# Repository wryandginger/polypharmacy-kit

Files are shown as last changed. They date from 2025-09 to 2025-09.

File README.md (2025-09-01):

# A 3D Printable Polypharmacy Kit
This is designed to be a sustainable and self-managed version of [polypharmacy](https://en.wikipedia.org/wiki/Polypharmacy) services by PillPack, SimpleDose, MedPack, etc.

I needed to create this because all of these services have shut down (or become significantly worse) due to late-stage capitalism, [enshittification](https://en.wikipedia.org/wiki/Enshittification), and unsustainable business practices. 

In my case, Amazon's aquisition and integration of PillPack has resulted in some of my medications now being "ineligible" for PillPack without warning or alternatives.
For a service designed for folks who need medication management help, (i.e. the elderly and chronically ill) this is deeply disappointing and frustrating.

The goal with this project is to have a whole medication system that functions like PillPack, but wastes less plastic and gives Amazon less of your personal data.

This is an elaborate remix of [TOXXIC407's Pill Organizer](https://www.thingiverse.com/thing:6817349), but significantly smaller (60%) in size and a few extra parts.

I tested this on a FlashForge Adventurer 5M Pro using natural PLA and Food Safe PLA printed at .12mm Fine Settings with 15% infill. 
I recommend using certified Food Safe PLA for obvious reasons, but I'm not a medical doctor or a lawyer, so you print at your own risk.

I'm mostly posting this because I have a habit of deleting and overwriting project STL files and I don't want to lose this (again).

# Instructions
1. Download the pillbox_daybase.stl and monday.stl files
2. Verify that the size is what you want. (This can hold about 9 small RX tablets, but you may have bigger pills.)
3. Scale up as needed. (This is as small as possible, increasing the scale should work without much issue.)
4. Print the base and Monday lid on your 3D printer. Verify that things fit together the way you want.
5. Print 28 more bases
6. Print 3 more Monday lids, print 4 Tuesday lids, 4 Wednesday lids, etc. until you have 28 lids for 28 bases.
7. Print 4 casettes and 4 casette lids
8. (Optional) Print a blank lid for an extra day.
9. (Optional) Print 1-4 medtrays to help with refilling or acting as a 1-week home caddy.

# Assembly and Use 
1. Slide your lid on to each box and make sure no box is cracked. I recommend assembling each box right as the lid finishes printing to minimize warping.
2. Each casette holds one week of medication in a small pocket sized box. (Consider printing a label with RX numbers and medication names for travel)
3. Neatly stack 7 days, with the first day at the bottom. Slowly slide the casette over 7 days, then tilt and close with the lid.
4. Dispense by removing the lid and tilting toward your hand like you would serve candy. Each day should dispense individually from the casette almost like a pez dispenser, but using gravity.
5. Repeat this 4 times to produce 4 casettes with 28 days of pre-sorted medication, 5 times gives you space for 35 boxes, etc.
6. (Optional) Use a [tilt or vibration sensor](https://www.amazon.com/Aqara-Vibration-Sensor-Automation-Compatible/dp/B07PJT939B/) to track and verify medication compliance (sample automation YAML coming soon)

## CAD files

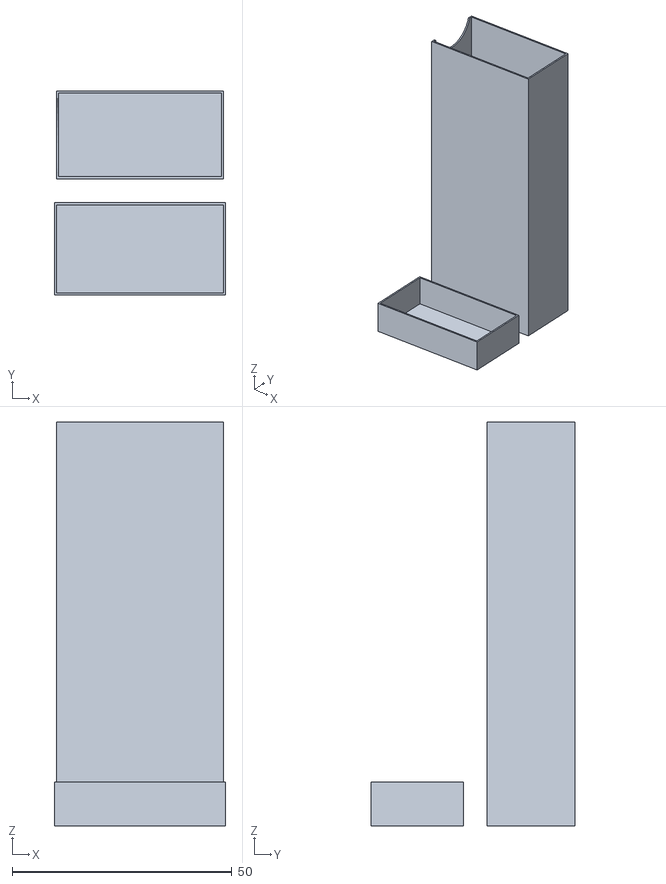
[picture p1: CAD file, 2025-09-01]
casetteandlid.stl
39.0 x 46.4 x 91.9

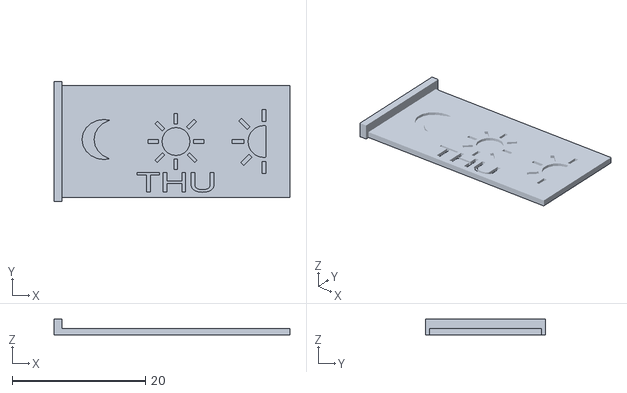
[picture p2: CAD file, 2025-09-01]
thursday.stl
35.4 x 18.0 x 2.40

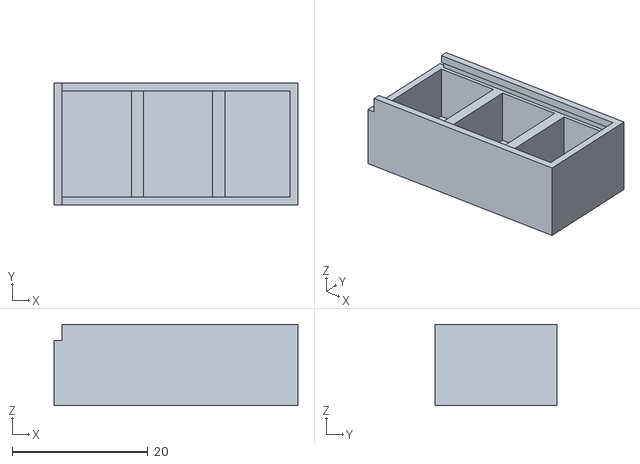
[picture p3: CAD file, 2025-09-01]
pillbox_daybase.stl
36.0 x 18.0 x 12.0

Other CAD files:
tuesday.stl
wednesday.stl
friday.stl
saturday.stl
monday.stl
sunday.stl
